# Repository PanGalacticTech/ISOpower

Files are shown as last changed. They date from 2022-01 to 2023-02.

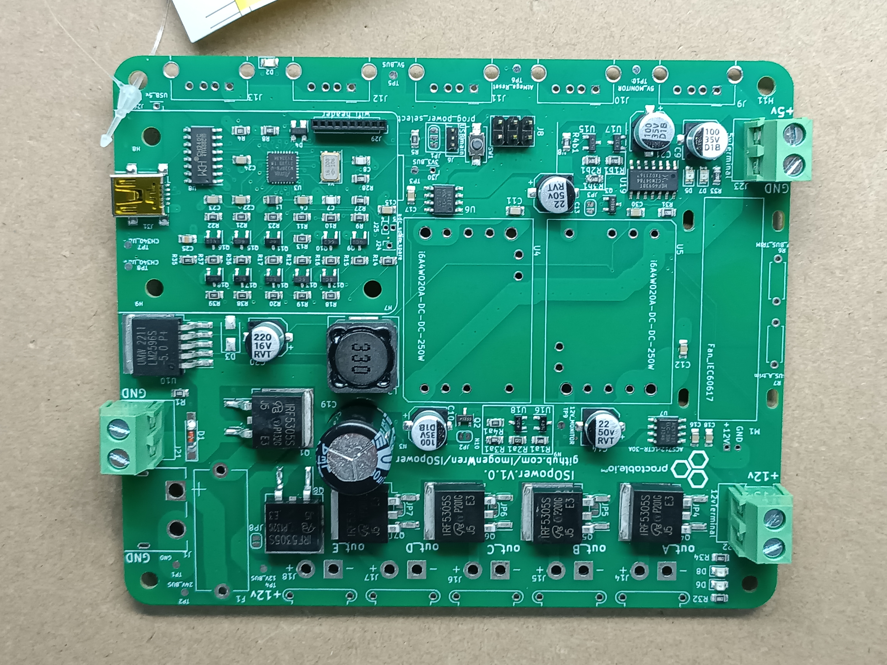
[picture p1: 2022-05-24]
Fabrication/Production Photos/Sample pictures of order T-Y4W418135A/IMG_20220523_194754.jpg

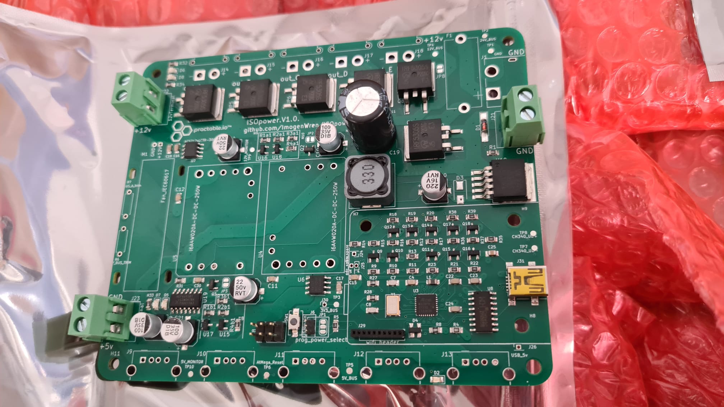
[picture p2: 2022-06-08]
Fabrication/Production Photos/Delivered Boards/ISOpower PCBs Delivered (1).jpeg

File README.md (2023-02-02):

# ISOpowerProject
 Remote power control board for ISO experiment containers, used for remote labs projects
ISOpower
ISOpowerPCBdesign

## Use

### Programming [See Issues]
 To Program AtMega328pb use the following settings:
 

### prog_power_select

- Jumper is used for power routing during programming
- Cut trace to main and solder USB to center to enable USB power during programming.
- Ensure to remove USB side and replace main for normal use

## Issues V1.0

1. Tx & Rx Pin swapped on CH340 - aTmeGA328P
 - To enable USB communication, reverse pins 2 & 3

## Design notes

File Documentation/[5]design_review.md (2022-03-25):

# PCB Design Review - [Project Title] 

_A form to document and record the PCB design review after completing layout in PCB editor._ 

## Design Review Notes

1. What Verification & Validation checks have been/can be carried out?
2. DRC Violations?
3. Will design solve problems?

## DRC - Design Rules Check

_Note down any DRC failings, the solution to remove them or reason for ignoring_

#### Errors

6 Courtyard overlap Errors
 - No solution required as conflicting footprint is surface level & unpopulated.

#### Warnings

1 Track has unconnected end
 - Copper layer is acting as heatsink
 
4 Footprint has no courtyard
 - Applies to silkscreen logos only - Can be ignored.

## Required Documentation for Fabrication

For PCB Fabrication:

	- Gerber files - In zipped folder [^gerber]

For PCB Fabrication, with component population:
	
	- Gerber files - in zipped folder [^gerber]
	- BOM [^1]
	- CPL Component Placement List / PNP Pick & Place File[^2]

### Documentation Checklist

|PCB				| Folder		|Files				| Checked 	| Checked Via 	|
|----				|----			|----				|----		|----			|
|	ISOpowerPCB		|zipped gerbers	|F_Cu.gbr			|	[]		|				|
|					|				|In1_Cu.gbr			|	[]		|				|
|					|				|In2_Cu.gbr			|	[]		|				|
|					| 				|B_Cu.gbr			|	[]		|				|
|					|				|F_Mask.gbr			|	[]		|				|
|					|		 		|B_Mask.gbr			|	[]		|				|
|					|				|F_Silkscreen.gbr	|	[]		|				|
|					|				|B_Silkscreen.gbr	|	[]		|				|
|					| 				|F_Paste.gbr		|	[]		|				|
|					|				|B_Paste.gbr		|	[]		|				|
|					| 				|Edge_Cuts.gbr		|	[]		|				|
|					|				|PTH.drl			|	[]		|				|
|					|		 		|NPTH.drl			|	[]		|				|
|					|ISO_power_PCB	| BOM.csv			|	[]		| 			|
|					|ISO_power_PCB	| top-pos.csv		|	[]		| 				| 
|----				|----			|----				|	----	|----			|
|ISOpowerWiFi_PCB	|zipped gerbers	|F_Cu.gbr			|	[X]		|				|
|					|				|In1_Cu.gbr			|	[X]		|				|
|					|				|In2_Cu.gbr			|	[X]		|				|
|					| 				|B_Cu.gbr			|	[X]		|				|
|					|				|F_Mask.gbr			|	[X]		|				|
|					|		 		|B_Mask.gbr			|	[X]		|				|
|					|				|F_Silkscreen.gbr	|	[X]		|				|
|					|				|B_Silkscreen.gbr	|	[X]		|				|
|					| 				|F_Paste.gbr		|	[X]		|				|
|					|				|B_Paste.gbr		|	[X]		|				|
|					| 				|Edge_Cuts.gbr		|	[X]		|				|
|					|				|PTH.drl			|	[X]		|				|
|					|		 		|NPTH.drl			|	[X]		|				|
|					|ISO_wifi_PCB	| BOM.csv			|	[X]		|	All Parts In Stock JLC PCB			|
|					|ISO_wifi_PCB	| top-pos.csv		|	[X]		|	checked against BOM			|

## Fabrication Notes

- Keep track of Component Stock, is it required for external fabrication, or purchased seperatly for manual assembly?

- JLC offer for free, specific location for their manufacturing number. Specify with "JLCJLCJLCJLC" on the silkscreen level.

## TODO

# Notes

[^gerber]: List of commonly used file names & formats, accepted by the majority of fabrication houses:
			- F.CU

[^1]: BOM Bill Of Materials
Reccomended formats: .csv, .xls, .xlsx
Example:
| Comment	| Designator	| Footprint | JLCPCB Part # (optional) 	|
|---		|---			|---		|---						|
|	100nF	|  C1			| 0805		|C49678 					|
|	22u		|  C2-5			| 6.3x5.4	|C72505						|
|	100uF	|  C6, C8, C10	| 6.3x7.7	|C65221						|

[^2]: Pick & Place or CPL File <br>
The Pick & Place File must contain the information below:

-	Designator - Component Reference Designator (e.g. C1, L2, R3)
- 	Mid X/Mid Y - The X/Y coordinate of the component centroid. Recommended units: Metric(mm). 
-	Layer - Top / Bottom, the board side where the component should be placed. 
-	Rotation - The rotation of the component given in degrees. Positive values are counter clockwise.
-	Recommended File Format: .csv, .xls and .xlsx.
Example:
| Designator 	| Mid X 	| Mid Y 	| Layer 	| Rotation 	|
|--				|---		|---		|---		|---		|
|	C1			| 95.0518mm	|22.6822mm	|	T		|	270		|
|	C2 			| 106.4056mm|33.2342mm	|	B		| 	90		|

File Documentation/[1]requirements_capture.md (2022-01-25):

# [1]   Requirements Capture Form - [Project Title]

_This form is intended to assist in capturing the requirements for new Open Source Embedded Systems Projects, <br>
its scope & implementation can be adapted to suit projects of varying complexity._

***************************************************************************************************************************************************************
## [1.1]Project Brief
_The project brief should contain an outline of the proposed project, with enough detail to derive a comprehensive list of requirements. The format, layout and
information provided can be tailored to project complexity_

### Example Project Brief - [ISOpower]

> PCB required to host DC-DC converters, to convert 24V DC power supply into operating voltages for ISO Experimental containers. 
> The containers house 4 experiments, each requires 12v for motor power, and 5v for raspberry pi via USB.
> Each USB 5v channel requires a power switch that can be actuated remotely.
> 
> Total current draw for 12v & 5v bus should be monitored via a microcontroller, with a interface allowing control
> over power switches on the board.
> Additional 5v & 12v power channel is required for future proofing, additional control infrastructure etc.
> 
> LED indication of correct voltage for 24v, 12v & 5v bus.
> Cooling should be provided for DC/DC Converters.
> Estimated power requirements set out in sub-system specification below.

#### Sub-Systems Specifications
##### Power Requirements
_Specific requirements for subsystems can be documented at this stage_    <br>
> a. steady power usage of 20W 1.7A at 12V (Maxxon AMax 32 236668 Graphite brushes, 20 Watt)[Estimated value, may change in future iterations] <br>
> b. peak power usage of 69W 5.7A at 12V (when motor stalled)  [Estimated value, may change in future iterations] <br>
> c. 5V power for the Raspberry pis, typically 2.5A per Raspberry Pi; four raspberry pi connections, 1 connection for power to microcontroller monitoring chip. <br>

##### Interface Requirements
> d. User interaction with system should be via JSON formatted commands with the ability to both poll specific data, and actuate switches.
> e. The system should report its status once per second. Minimum data for status update includes:
>    1. Current sensor readiings for 5v & 12v bus
>    2. Time since last reset in seconds. (Hint: Record number of times millis() rollsover) Integer should be able to record times >10 years (314496000 seconds)
> f. Any network communication should use TCP protocol, on port 443 to avoid firewall conflicts.
> g. Off nominal voltage detection should trigger a JSON message to be sent to the user. This reporting should be rate limited to avoid a single fault sending spam.
> h. System should track, and allow to be queried remotly:
>    1. How many times has the voltage tripped for out of spec performance
>    2. The last recorded time of a voltage fault
>    3. Include method for resetting count to 0 after fault has been rectified.

#### General Specifications/Requirements
_These specifications are going to be valid for most projects developed using this framework_
> 4. Circuit should be protected from reverse supply voltages. <br>
> 5. Circuit should be fuse protected <br>
> 6. 5v bus should be protected from over voltage conditions.

#### Optional Features
_Any features or functions that are optional should be stated here_  <br>
>  1. Report Status & current usage for sustainabilty and maintainance purposes.
>  2. Individual remote control of channel power.
>  3. Use only connection types that can be operated with one hand. i.e. avoid screw terminals.

#### Design Optimisation
_What parameters of the design should be minimised/maximised?_

#### Design Tradeoffs
_Space for discussion and weighing up of features that may or may not be required_ <br>

> If method is implemented to turn off power in the case of fault condition, provide some way of bypassing this feature
> to assist in debugging.

#### Quality Assurance 
_What quality assurances or requirements, if any, need to be established?_

#### Notes
_Any Extra Notes?_
Software Reqirements: 

### Existing Products & COTS (Consumer Off The Shelf)
_The project brief may also contain information on currently available similar products and a brief description of the features they lack and a 
quick review of whether they can fullfill the aims of the project._

_______________________________________________________________________________________________________________________________________________________
## [1.2]High Level Requirements Description

*This section should contain a numbered list of all the specific high level requirements that can be gathered from the project brief, or from the client directly. <br>
High Level Requirements capture the intent and function of a system, without going into specifics of how these will be achieved or any specific implementations. I.E. They take a Black Box approach*

#### High Level Requirements should address:
> - Client Needs
> - Features & Functionality
> - Interfaces
> - Performance
> - Quality Attributes
> - Design Constraints
> - Regulations
> - Safety & Security
> - System

#### Requirements should be:
> - Specific           - Document a single feature or function requirement at a time.                                                 <br>
> - Quantifyable       - Provide quantifyable parameters, boundary limits of operation and/or design tolerences, rather than open ended specifications where possible.<br>
> - Self Contained     - Do not rely on assumptions to deliver information, as different engineers will make different assumptions, which may cause conflicts 
> - Traceable          - Assign each requirement an ID number, this will be used to trace any design decisions through the development process. <br>

_Good requirements are the foundation for successful development of a project, as it allows design decisions to be traced through the development process.
it also provides the information required to undertake successful **Verification** & **Validation**[^V&V]._ 

_______________________________________________________________________________________________________________________________________________________
## [1.3]Example Requirements Capture - [ISOpower]

> HL.1. DC/DC converters must be able to provide continuous current draw of 6.7A at 12V ~(80W) for motor power, from supplied 24v input.                   <br>
> HL.2. DC/DC converters must be able to provide peak current draw of 12A at 12V ~(144W) for motor power, from supplied 24v input, in case of stall condition.[^2]    <br>
> HL.3. USB power must be able to provide total of 12.5A @ 5v ~(62.5W), from supplied 24v input.                                  <br>
> HL.4. Each USB channel will have the ability to remotely disable and re-enable power.                                      <br>
> HL.5. Voltage & Current monitoring of 12v bus, accessable remotely.   <br>   <!-- This is a weak requirement, how often should data be sampled is a nessissary component of this requirement -->
> HL.6. Current monitoring of 5v bus, accessable remotely  <br>    <!-- This is a weak requirement, how often should data be sampled is a nessissary component of this requirement -->
> HL.7. Board must have push-fit or bayonet connectors for motors & offboard hardware. <br>
> HL.8. Power Board will have 5 * 12v outputs from 12v Bus. <br>
> HL.9. Power Board will have 5 * 5v outputs from 5v Bus. <br>
> HL.10. Power board will be protected from reversed supply voltages <br>
> HL.11. Power Board will be protected from over-current conditions<br>
> HL.12. PCB must have same footprint & mounting screwholes as V1, to aid in assembly <br>
> HL.13. 5v bus will be protected from over-voltage condition. <br>
> HL.14. Each power bus will display visual (LED) indication of correct operation or fault conditions (over/under voltage) <br>

<!-- NOTE: 
High level
Include a microcontroller which communicates over USB, with a JSON-based interface allowing control over any power switches on board, and can report any measurements made.
It is my understanding this is not a high level requirement, as it is a specific low level hardware & software requirement. I have modified some of the other requirements
 to make it clear that the data & power channel actuation should be accessable remotly, but have not gone into specifics of how that would be achieved-->

When to review? <br>
*High level requirements should undertake a review process,* ***Validation***, *to ensure they meet the clients needs, before any further development takes place.*<br> 

<!--After review, please see the next document in the design process* [[2]Low Level Requirements Capture](https://github.com/PanGalacticTech/project_template/blob/main/%5B2%5DLL_requirements_capture.md) -->

_______________________________________________________________________________________________________________________________________________________

[^V&V]: Verification & Validation - What is it? <br>
        - Verification - _"Does the implementation meet the requirements?"_ <br>
        - Validation   - _"Are the requirements correct"_
        
[^2]: Assumption made that only 1 motor will be in stall condition, with others running typically.

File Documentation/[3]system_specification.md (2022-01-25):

# [3]  System Specification - [Project Title]

_This form is intended to derive low level hardware & software specification from the ***Validated***  
High Level Requirements Capture Form [[1]requirements_capture.md](https://github.com/PanGalacticTech/project_template/blob/main/%5B1%5Drequirements_capture.md) and
[[2]system_optioneering.md](https://github.com/PanGalacticTech/project_template/blob/main/%5B2%5Dsystem_optioneering.md) <br>
Its scope can be adapted to suit projects of varying complexity_ <br>

****************************************************************************************************************************
## [2.2] System Specification Description

_System Specifications for Hardware & Software are derived from and traceable back to the High level Requirements. At this stage optioneering should be
complete, and the design direction finalised._

<!-- NOTE: Origionally I had this document specified as "Low Level Requirements" given past training I had on embedded systems development in aviation, however I 
think this approach was far in excess of what is required for this kind of project, so I have merged "low level requirements" and "system specification" into a single step -->

## [2.3]Example System Specification - [ISOpower]

### [2.3.1]Hardware Specification
_Hardware specification should outline specific hardware devices, circuit design and hardware archetectures chosen to meet high level requirements._

<!-- NOTE: Spreadsheet would be better for comparason of features of components but I see value in documenting major components here too? -->

_Hardware Specification may contain the following subsections:_
- Hardware Architecture
- Major Components - Can be specific or requirements set out for comparason of specific components
- Circuit Design
- Other

### Hardware Architecture & Description

**[HL.1, HL.2, HL.3]**
> The hardware will comprise of a single PCB to home the 2 DC/DC converter modules. 
> These require local fan cooling for which +12v power and mounting holes will be provided.

**[HL.7]**
> 24v Power input will be via XT60 Connector mounted directly on PCB. 

**[HL.5]**
> MCU will be AtMega328p integrated to PCB with ESP32-WROOM-32UE as a WiFi tranciever. MCU will take ADC readings from 2 [Allegro ACS712](https://www.sparkfun.com/datasheets/BreakoutBoards/0712.pdf) current sensing modules,
> one between the DC/DC module and the 12v bus, the other between the 2nd DC/DC module and the 5v bus. Each MCU 

**[HL.5, HL.6]** 
> A voltage divider will be used with an additional ADC input to monitor the voltage of the 12v bus. <br>
> - R1: 100k <br>
> - R2: 56k <br>
> This will allow measurements from 0v to ~14v to be measured by the microcontroller ADC, while limiting current draw to a few microamps.
> Input to the MCU will be protected by a 5.1v Zener diode, incase of voltage spikes greater than can be mitigated by the voltage divider.

**[HL.9, HL.4, HL.13]**
> The 5v Bus will be distributed to 5 USB outputs via individual high side MOSFET switches for each channel,
> these will be connected source to 5v bus, drain to USB output, and gate to the logic circuit used to 
> trigger a power shutoff condition.
> 
> Solder bridges will be provided on the PCB to bypass these MOSFETs, in the case they are not required.

**[HL.4, HL.13]**
> Logic circuit to control power to each 5v USB output will follow the following logic, if: <br>
> A = microcontroller digital pin (1 per channel, logic level HIGH = channel deactivated) <br>
> B = Voltage Monitoring circuit (1 per +5v Bus, logic level HIGH = off nominal voltage detected)  <br>
> C = Output to MOSFET gate (1 per channel, logic level HIGH = MOSFET OFF state) <br>

> IF A OR B == HIGH: C = HIGH.

**[HL.13]**
> The voltage protection circuit will comprise of 2 TL431 Voltage reference ICs set as a window comparator. This circuit will
> output logic level LOW in the case +5V_BUS is pulled off nominal. (4.6v - 5.5v).
> 

**[HL.7, HL.8]**
> 12v bus power will be distributed to 5 XT30 connectors, mounted directly on the PCB. 

 **[HL.10]**
> Reverse voltage protection will be acheived via a P channel MOSFET[^RevVolt] at +Vcc in.

**[HL.11]**
> The system will be protected from overcurrent conditions by a 20A fuse between Vcc in+ and 24v bus. 

**[HL.12]**
> PCB dimensions will be 100x120mm. 

**[HL.14]**
> LM3916 Dot graph drive IC will be used on each voltage bus, 5v, 12v and 24v. Some experimentation may be required to select the correct
> circuit layout & resistor selection for each application. 24v bus will require additional voltage divider,<br>
> R1: 100k <br>
> R2: 56k <br>
> to scale voltage to correct input for LED driver. 24Vin =~ 8.6Vout

_Optional:_
> The PCB will contain footprints to allow 12v outputs to be switched via additional MOSFETs, as well as solder bridges to enable the PCB to be used without. [Dependent on overall size & space left after all other requirements have been met]

-----------------------------------------------------------------------------------------------------
### Major Components

#### DC/DC Converters
##### Option 1: <br>
**Non-Isolated DC-DC Converter, 3.3 → 15V dc Output, 20A**
| Attribute          	|  Value 	                            |  Notes
|---	                |---	                                |---
| **Part Number:**   	| I6A4W020A033V-001-R               	| 
| **Supplier:**     	| RS Components                      	|   
| **Vin:**          	| 9 - 40v                            	|   	
| **Vout:**           |  3.3 - 24v                          |   
|**Power:**            |    250W                            |     
| **Price:**           |  £44.66                            |   
| **URL:**              | https://uk.rs-online.com/web/p/non-isolated-dc-dc-converters/1813289    |     
| **Notes:**           | -     |    
|**Requirements Met:**  |  (HL.1, HL.2, HL.3)        |

#### P-Channel MOSFET for Channel Switching
_Use: High side power switch_
1. Switching of 5v USB power from bus to individual outputs
2. Switching of 12v power from bus to individual outputs (optional feature)
3. MOSFET is ON when gate is @ 0v, OFF when gate is driven to VDD

_Component Requirements:_
| Attribute | Value        | Notes |
|---        |---           |---    |
| Vds        | > (-)21V      | Drain/Source Breakdown Voltage = Operating Voltage + 70% |
|Id         | > (-)6A        | Max Continuous Drain Current > Stall Current of Motor |
| Vgs       | ~ -4.5       | Gate - Source Threshold Voltage[^Vgs] |
| Rds(on)   | <2 ohm       | Static Drain-to-Source-ON-Resistance[^Rds] @ Vgs |

_In the case the requirements for a component are known, however the specific part is unknown, it would be best to use a [spreadsheet](https://github.com/PanGalacticTech/project_template/blob/main/%5B2A%5Dcomponent_compare.xlsx) to weigh up alternative options._

##### Option 1: <br>
**IRF5305PBF P Channel MOSFET**
|Attribute        | Value                                            |Suitable  | Notes |
|---              |---                                               |---       |---    |
|Part Number:     |  IRF5305PBF                                      |          |       |
|Supplier:        | Farnell                                          | [x]      |       |                 
|Vds              |  -55V                                            | [x]      |       |     
|Id               |  -31A                                            | [x]      |       |  
|Rds(on) @ -10v   |  0.06                                            | [x]      |       |      
|Price:           |  £2.088                                          | [x]      |       |      
|                 |                                                  |          |       |
|URL:             |  [IRF5305PBF - Farnell](https://uk.farnell.com/infineon/irf5305pbf/mosfet-p-55v-31a-to-220/dp/8648255) |         |        |
|Availability     |   In Stock                                       | [x]       |       |
|Notes:           |  |         |       |                                                                            
|Meets Requirements: |                                               | [x]     |       |

#### P-Channel MOSFET for Reverse Volatage Protection
_Use: Reverse voltage protection_
1. MOSFET is ON when gate is @ 0v, OFF when gate is driven to VDD

_Component Requirements:_
| Attribute | Value        | Notes |
|---        |---           |---    |
| Vds        | > (-)21V      | Drain/Source Breakdown Voltage = Operating Voltage + 70% |
|Id         | > (-)6A        | Max Continuous Drain Current > Stall Current of Motor |
| Vgs       | ~ -4.5       | Gate - Source Threshold Voltage[^Vgs] |
| Rds(on)   | <2 ohm       | Static Drain-to-Source-ON-Resistance[^Rds] @ Vgs |

_In the case the requirements for a component are known, however the specific part is unknown, it would be best to use a [spreadsheet](https://github.com/PanGalacticTech/project_template/blob/main/%5B2A%5Dcomponent_compare.xlsx) to weigh up alternative options._

##### Option 1: <br>
**IRF5305PBF P Channel MOSFET**
|Attribute        | Value                                            |Suitable  | Notes |
|---              |---                                               |---       |---    |
|Part Number:     |  IRF5305PBF                                      |          |       |
|Supplier:        | Farnell                                          | [x]      |       |                 
|Vds              |  -55V                                            | [x]      |       |     
|Id               |  -31A                                            | [x]      |       |  
|Rds(on) @ -10v   |  0.06                                            | [x]      |       |      
|Price:           |  £2.088                                          | [x]      |       |      
|                 |                                                  |          |       |
|URL:             |  [IRF5305PBF - Farnell](https://uk.farnell.com/infineon/irf5305pbf/mosfet-p-55v-31a-to-220/dp/8648255) |         |        |
|Availability     |   In Stock                                       | [x]       |       |
|Notes:           |   DO NOT USE FOR REVERSE POWER PROTECTION ON 24V BUS. Vgs Max is 20v|         |       |                                                                            
|Meets Requirements: |                                               | [x]     |       |

#### AtMega328P MCU

#### Allego ACS712

#### 
-----------------------------------------------------------------------------------------------------

### Circuit Design & Schematic
_Final Circuit Design, Schematics & Justifications for design_

_____________________________________________________________________________________________________
 
#### [2.3.2]Software Specification

_Specify the software requirements, functions, frameworks and tools required to meet the high level requirements_

#### Tools:
| Tool | Purpose | Justification |
|---   |---      |---            |
|Arduino IDE| Software Development | Speed & ease of development for Arduino IoT functions |
|C++ | Programming Language | Native to Arduino environment |
|InfluxDB | Remote storage of power consumption data | Ease of setup & ease of posting data from remote devices |
|Grafana  | Graphic display of power consumption via web interface | off the shelf solution that can integrate control methods for sending HTTP requests back to controller |

### Software Specification

- ADC Samples of current sensor will be taken every 250mS  <!-- Let me know if these timings are suitable  -->
- ADC samples of 12v bus voltage will be taken every 250mS <!-- Let me know if these timings are suitable  -->
- Power Channel MOSFETS are "Active Low" Therefore channels will be turned off driven by a HIGH pulse from microcontroller.
- Seperate API for each power channel "on", "off" and "restart",

When to review? 
*System Specification should undertake a review process, to ensure the design meets the clients needs before moving to ***Fabrication*** <br>*

_______________________________________________________________________________________________________________________________________________________

### [2.4] Requirement Matrix

_Info On Requirements Matrix & Link to: [Requirements Matrix Document](https://broken_link.com)_

_______________________________________________________________________________________________________________________________________________________
#### References

- [Rugged Circuits: 10 Ways to Destroy an Arduino](https://www.rugged-circuits.com/10-ways-to-destroy-an-arduino)
- [High Side vs Low Side Switch](https://www.baldengineer.com/low-side-vs-high-side-transistor-switch.html)
- [Important Stuff: MOSFET Specs You Need to Know](https://www.embeddedrelated.com/showarticle/809.php)
- [Using the Atmel ATmega328P Analog to Digital Conversion Module](https://ece-classes.usc.edu/ee459/library/documents/ADC.pdf)

*******************************************************************************************************************************************************

#### Notes
**VGS & Rds Explanation**

_Assuming That_

|Attribute | Value | Max Current Flow
|---|---|---|
| Source Voltage | 5v |
|Rds(on) @ Vgs -4.5v | 0.0133 ohm      | 5/0.0133 = 376A |
|Rds(on) @ Vgs -10v   | 0.0083 ohm      | 5/0.0093 = 537A  |

#### Footnotes

[^Rds]: Drain-to-Source On-Resistance <br>
        - If current required is 2.5A, then R=5/2.5: R=2ohm absolute max Rds during operation (in practice must be much lower)   <br>
        - If Vcc = 5v, and gate is pulled to 0v GND, then Vgs ~-5v                                                                <br>
        - Datasheet shows Rds(on) @ Vgs -4.5 will be ~ 0.0133 ohm                                                                     <br>
        - If Vcc = 12v & Gate is pulled to 0v GND, then Vgs ~ -10v therefore Rds(on) ~ 0.0093 ohm                                                       <br>
        - HOWEVER, controller can only provide 5v so will need drivers to fully turn off MOSFET, see[^Vgs(th)]                              <br>

[^Vgs(th)]: Gate-Source Threshold Voltage <br>
            - Datasheet shows that Vgs must be >-2.0V to turn off device  <br>
            - i.e. Id = -250 uA @ Vds (Maximum Drain - Source voltage differential) <br>
            - Therefore if VCC is 12v, Gate Voltage must be driven to >10v to turn off MOSFET <br>

[^V&V]: Verification & Validation - What is it? <br>
        - Verification - _"Does the implementation meet the requirements?"_ <br>
        - Validation   - _"Are the requirements correct"_
        
<!--[^2]: Ruggeduino >5v cutoff circuit -->
      <!-- - ![image](https://user-images.githubusercontent.com/53580358/148758688-282c6b19-230f-4211-98ce-a5ba380fc2d2.png) -->
          
<!-- [^3]: Estimated current consumption of cutoff circuit
      - R = 17kohm, V = 5v. 
      - I=V/R
      - I = (17k / 5) = [2.9\*10^-4] A -->
      
[1v1]: [Arduino: Analog Reference](https://www.arduino.cc/reference/en/language/functions/analog-io/analogreference/)

[^RevVolt]: [Infineon Reverse Voltage Protection Methods](https://www.infineon.com/dgdl/Reverse-Batery-Protection-Rev2.pdf?fileId=db3a304412b407950112b41887722615) <br>
             

[^zener]: [Designing overvoltage protection using zener diodes](https://components101.com/articles/designing-an-overvoltage-protection-circuit-using-zener-diodes)

[^comp]: [op-amp comparator](https://www.electronics-tutorials.ws/opamp/op-amp-comparator.html)

[^vu]: [Single Transistor LED VU meter](https://electronicsarea.com/6-led-vu-meter-using-one-transistor/) <br>

[^uvov]: [LM431 Datasheet](https://www.ti.com/lit/ds/symlink/lm431.pdf?HQS=dis-dk-null-digikeymode-dsf-pf-null-wwe&ts=1642092638827&ref_url=https%253A%252F%252Fwww.ti.com%252Fgeneral%252Fdocs%252Fsuppproductinfo.tsp%253FdistId%253D10%2526gotoUrl%253Dhttps%253A%252F%252Fwww.ti.com%252Flit%252Fgpn%252Flm431) <br>  <br>
<!-- ![image](https://user-images.githubusercontent.com/53580358/149550148-76459666-dd3e-4661-bf27-dfcf147a4180.png) <br> -->

[^tl431]: Voltage Window Calculations: <br>
          - Vh=(1+(R2/R)1)*Vref   <br>
          - Vl=(1+(R4/R3))*Vref

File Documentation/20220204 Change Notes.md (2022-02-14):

# Change Notes

04/02/2022
As per discussion 26/01/22
1. Changed per channel 5v MOSFET switches to MOSFET control of DC/DC module on/off pin - due to failure of MOSFET switching during testing.
2. Added 5v buck converter for independent MCU_5V power bus.
	- Ensured all 5v MCU hardware is powered from common MCU_5V bus.
3. Removed circuit from NC pins on DC/DC modules.
4. Changed ESP32 USB interface to CH340
5. Changed MCU serial logic level converters from MOSFET to IC - TXS0102DCT
	- TODO: OE pin now requires low signal untill DC/DC supply is stable - Does it? Can it just be tied to 5v bus with a large capacitor? Does it need MCU to hold pin low untill 5V_BUS is stable?
6. Removed redundent 3V3_IN to power distribution page.
	- Rechecked all sheets for redundent pins, it won't impact drawing traces, but it will impact readability.
7. Added Mechanical layer as hirarchical sheet.
8. Moved voltage monitoring circuits to hirarchical sheet
9. Added voltage monitoring with TL431DBZ to 12V_BUS
10. Automatic shutoff circuit removed, as this would prevent the DC/DC module from powering on. Instead moved to AtMega328p digital inputs
and microcontroller will control shutdown of DC/DC supply if out of spec voltage detected.
		- This is a severe limitation compared to the specification, and this also does not prevent damage to devices on 5V_BUS if voltage is pulled high, for example to 12v due to user error.
		- TODO: Add independent overvoltage protection to 5V_BUS? 		[Zener Diode Overvoltage Protection - Sparkfun](https://www.rs-online.com/designspark/how-does-zener-diode-do-overvoltage-protection-in-circuit#:~:text=In%20order%20to%20protect%20the,flow%20in%20the%20reverse%20direction).
11. Changed logic level conversion for 12v outputs to 12v drive circuit. [12v drive circuit](https://forum.arduino.cc/t/easiest-way-of-driving-amplifying-from-5v-to-12v/123290)
12. Added proto pin connections for ESP MCU.
13. Changed 20v Zener in reverse voltage protection to 18v

## TODO
- TODO: OE pin now requires low signal untill DC/DC supply is stable - Does it? Can it just be tied to 5v bus with a large capacitor? Does it need MCU to hold pin low untill 5V_BUS is stable?
- TODO: Add independent overvoltage protection to 5V_BUS? 		[Zener Diode Overvoltage Protection - Sparkfun](https://www.rs-online.com/designspark/how-does-zener-diode-do-overvoltage-protection-in-circuit#:~:text=In%20order%20to%20protect%20the,flow%20in%20the%20reverse%20direction).
PROBLEM: Suggested 100r resistor between 5v and raspberry pi, this limits current to 50mA, raspi requires min 400mA (Tested with raspi 512mb, raspi4 will likely require more current) if R=12.5 is selected, Imax would be 400mA, however power disspation in the resistor is now 0.4\*5 = 2W.
- TODO: Nominal Voltage Indication?

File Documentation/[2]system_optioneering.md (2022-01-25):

# [2]  System Optioneering - [Project Title]

_This form is intended to assist in optioneering to derive low level hardware & software specification from the ***Validated***  
High Level Requirements Capture Form [[1]requirements_capture.md](https://github.com/PanGalacticTech/project_template/blob/main/%5B1%5Drequirements_capture.md).
Its scope can be adapted to suit projects of varying complexity_ <br> 
*******************************************************************************************************************************************************

## [2.1] Design Tradeoffs & Optioneering
_Space to work through different options before deciding on specific low level requirements & system specification for hardware & software
It is useful to highlight situations where one design decision is dependent on other decisions, or where a design decision will have known, or forseeable impacts on
other decisions later._

### Preamble
_Introduction to the design approach if required_ <br>

### Optioneering Diagrams
_Flowcharts can be used to explore the relationships between different options, and display graphically how making specific design decisions
will affect the other available options._

hardware optioneering diagram
_Flowchart showing the different communications standards and methods that could be used to connect the user interface and the microcontroller, dependent on
low level hardware choices_

### Optioneering Table
_This is an example of the options that may wish to be explored for this project, however there may be alternative ways of displaying this information
that are more suitable_

|Requirement| Function                      | Options                       | Sub-Options                                | Hirarchy  | Notes  |
|---        | ---------------------------   | ---------------------------   | -----------------------------------------  | -------   |----    |
|HL:(4,5,6) | Controller for Current Sensing| Integrated MCU on PCB         | CH340 Driver for USB comms to Raspi        |    3      |        |
|"          |           "                   |           "                   | ublox Wifi module & remote database server |    2      |        |
|"          |           "                   |           "                   | ESP32 performs as MCU controller And/Or Wifi Module|    1   |  requires 3.3v logic if used as MCU|
|"          |           "                   | Arduino Nano 33 IoT| Local Raspberry Pi |    4    | will require 8 port switch to accomidate extra RasPi in ISO Container | 
|"          |           "                   |    "             | Remote Raspberry Pi  |    3    | Will Require external WiFi Antenna to ensure robust Connection|
|           |                               |                               |                                            |           |        |
|HL:(4)     | Power Switching               |N-Channel Low Side MOSFET      |                                            |    3      |        |  
|"          |           "                   |P-Channel High Side MOSFET     |                                            |    1      | Difficult to source suitable MOSFET|  
|"          |           "                   |Relay                          | Normally Closed                            |    2      | Expense       |    
|"          |           "                   |           "                   | Latching                                   |    4      | Expense, Reliability       |      
|           |                               |                               |                                            |           |        |  
|HL:(1,2,3) | Power Supply DC/DC Conversion | COTS Modules                  |                                            |     1     |        |    
|"          |           "                   | ReEngineer & Integrate w/ PCB |                                            |     4     |        |  
|"          |                               |                               |                                            |           |        |
|HL:(7)     | Power Input Connector         | Screw Terminals               |       |  4  |                                             |
|"          |         "                     | XT60 - 60A  Connector         |       |  1  | Quick Disconnect Compared to screw terminals, easy to solder, easier PCB mounting|
|           |                               |                               |                                            |           |        |  
|HL:(7)     | 12v Power Output Connectors   | 2.1mm Barrel Jacks            |       |  4  | Hard to find with range of options, easy to damage|
|"          |           "                   | XT30 - 30A Connector          |       |  1  | Easy to source, many differnt options, well defined specifications|
|           |                               |                               |                                            |           |        |  
|HL:(5)     | Voltage Sensing               | Voltage Divider on 12 bus   | | 1 | Can't be used for 5v bus as MCU would share Vcc ref. Must protect MCU from voltage spikes|
|"          |     "                         | Voltage sense IC            | | 2 | Cant find suitable option, open for reccomendations, could be used for both 12v and 5v bus|
------------------------------------------------------------------------------------------------------------------------------------------------------------------------------

### Circuit Design & Hardware Optioneering [Hardware]
_Exploration of circuit elements & Hardware that might be used to meet design objectives_

#### Overvoltage Protection of 5v USB Bus ***[HL.13]***
_The aim of overvoltage protection for the 5v bus, is to protect the raspberry pis in the event +12v power is accidently applied to this bus, pulling all the outputs to 12v
and causing damage. Several possible approaches will be discussed below_

##### Approach 1 - Zener Diode

>    5.1v zener diode reverse biased between the USB outputs 5v rail, and GND.
>    A 100ohm resistor must be between the potential source of over voltage and the zener diode.[^zener]

***Problems with this approach***

>    If the source of the overvoltage is also on the USB bus, this does not nessissarily solve the problem,
>    as the current will flow unimpeded through the zener diode, causing overheating and component failure. 
>    If it fails open circuit (likely) then the protection is no longer active and the 5v bus will be pulled to 12v.

> As the likely source of the overvoltage would be the other USB inputs, each V+ rail would need a 100ohm resistor, with a zener diode on the supply side of the resistor.

##### Approach 2 - Using the MOSFET That is Already There

>    As the USB channel is already designed to be switched off via a logic high signal (+5v) from a microcontroller, 
>    could that same MOSTFET also be triggered with logic high if a fault condition is detected?
>    This solution would have to be passive, i.e not be reliant on the MCU to trigger, as this
>    would delay response and would not stop damage from occuring.
>     <br>
>     A logical OR gate could be used to provide a buffer between the logic HIGH/LOW pin on the microcontroller, and the
>     other system for providing a logical HIGH in the case the 5v bus moves out of tolerance. 1 logical OR gate would be required for each USB output,
>     The output of each logic gate, feeds the gate of each MOSFET

***OverVoltage Detection***

> Voltage Supivisor/detection ICs: <br>
> [TL431 Voltage Reference, Adjustable Shunt](https://uk.farnell.com/on-semiconductor/tl431acdg/voltage-ref-shunt-2-495v-36v-soic/dp/1651199)<br>
>  Voltage is monitored on 5v rail, and IC outputs a logic high if voltage goes outside of set nominal band. <br>
>  
> **Use Case**
> [TI TL431 for Under & Overvoltage Detection]( https://www.ti.com/lit/an/slva987a/slva987a.pdf?ts=1642107195143&ref_url=https%253A%252F%252Fwww.google.com%252F)[^uvov]
> In this case, the V(high) and V(low) thresholds are set via 4 resistors. Calculations outlined below[^tl431] 

> TL431 has a minimum cathode current of 1mA, so resistor selection must be checked to meet this requirement.

> Resistor Values Estimated:
> R1: 470r      <br>
> R2: 560r     <br>
> Vhigh ~ 5.47v   <br>
> <br>
> R3: 560r   <br>
> R4: 470r   <br>
> Vlow ~ 4.8v
>
> R5 = 220r <br>
> <br>
> Using these values & <br> I = (Vcc - Vref)/R3 (High edge) & I = (Vcc - Vref)/R5 (Low edge) [No sure if correct best guess given forum posts & datasheet] <br>ere
> Ika ~ 4mA for high edge & 11mA for low edge

***Implementing This Solution***
> Requires: <br>
> 5 * OR Gates <br>
> > <br>
> To make these gates from common gates, it would require: <br>
> 15 * NAND Gates. (3 req for OR gate) <br>
> OR <br>
> 10 * NOR Gates. (2 req for OR gate) <br>
> Suggest: <br> 
> 3 * [MC74HC02ADG SMD Quad Input NOR Gate](https://uk.farnell.com/on-semiconductor/mc74hc02adg/ic-74hc-cmos-smd-74hc02-soic14/dp/9666893)

---

#### Power Bus Visual Fault Indications ***[HL.14]***
_The aim of this requirement is to provide additional information to engineers testing, maintaining and debugging the system. For this
reason it should be independent of all other systems, and simplified as much as possible._

>   I much prefer the idea of independent indication for each bus, rather than a traffic light with 
>   "All Nominal" "Something Off Nominal" "Everything Off Nominal" indication, as I believe this is; <br>
>   1: less useful than say "A Okay" "B Okay" "C Okay" indications and <br>
>   2: it may also be harder to design if we take a passive approach, i.e: This system should work independently
>   of any microcontrollers.

##### Option 1

>   A window comparator circuit[^comp] could be used to display whether each bus is falling within a predefined "nominal" window,
>   however this circuit would be reliant on stable Vcc, so is not useful for detecting if Vcc is off nominal.
>   An independent linear or LDO regulator could provide independent reference voltages to solve this problem, but 
>   increase in cost & complexity.

##### Option 2

> Led VU Meter, Options detailed [^vu]  [LM3916 Dot/Bar Display Driver](https://cdn.sparkfun.com/datasheets/Components/General%20IC/lm3916.pdf) Monitors 
> analog voltage level and lights up to 10 LEDs sequentially
> Supply Voltage from 3v to 25v - Suggest it runs from 12v rail for each use case. Input can handle from 0 to 35v 

***Assessment***
This option did not work well, as the window for the "okay" LED was far too wide, I managed to get it to indicate high voltage at 5.5v, however getting it to register
low voltage at anything >4v seemed to fail. It also did not perform well with off nominal supply voltage.

#### Option 3
> Use the features of the DC/DC supplies[^dcdc]

> DC/DC supply can indicate an off nominal voltage rail by pulling a logic HIGH to ground. This can be monitored by the MCU and set error LEDs. This will also enable easy 
> reporting & monitoring of power status.
> Can be used for visual indication lEDs & report via JSON.

---

#### MCU Selection

The best options for MCU seem to be either;
[AtMega328p](https://uk.farnell.com/microchip/atmega328p-an/mcu-8bit-atmega-20mhz-tqfp-32/dp/2443178?st=ATmega328P) combined with CH340 for USB comms & programming, ISP header for programming bootloaders, and an WiFi transcever as a peripheral device, or <br>

[ESP32-WROOM-32U](https://www.mouser.co.uk/ProductDetail/Espressif-Systems/ESP32-WROOM-32UM113DH3200UH3Q0?qs=W%2FMpXkg%252BdQ4Fqx%2FReRQpFQ==&mgh=1&vip=1&gclid=CjwKCAiAxJSPBhAoEiwAeO_fPwE6kImUAnBTI5SyodKJNS7nNKTfdQ13Md3OplGP5AphD8abym4PYBoCbGkQAvD_BwE), with the same USB interface and ISP header, but without the need for an additional WiFi transcever. This has a number of advantages and disadvantages. 

The major disadvantage is the ESP's requirement for 3.3v logic, this will likely require additional drivers for actuation of the MOSFET switches,
as well as voltage dividers and additional scaling on ADC inputs from the [ACS712 Hall Effect Linear Current Sensor](https://www.sparkfun.com/datasheets/BreakoutBoards/0712.pdf)
For this reason, using the AtMega328p as the main MCU seems like it will cause less issues with the rest of the circuit design.

However the selection of the peripheral WiFi adaptor throws up an ironic aside, it seems much cheaper to use ESP32
as a WiFi device than sourcing dedicated WiFi transceiver modules like the ublox nina.
The ESP32 is available with the option to connect an external antenna, which makes the system more adaptable for use
in areas that may not have adiquate WiFi signal with the antenna obscured inside a metal box.

***Conclusion***

The board will use both AtMega328p to act as the hardware controller, and ESP32 to act as wifi & higher level control. This will also act as a proving ground for using 
mixed controller boards, interfacing ESP32 with other MCUs, and potentually offering up the ability to expand the scope of the power supply module later with more advanced 
software run on the ESP32, with the AtMega handling the lower level hardware monitoring.

[Info on using ESP32 as WiFi adaptor for AtMega328p](https://icircuit.net/arduino-interfacing-arduino-uno-esp32/2134)[^esp32]

****************************************************************************************************************************

### Software Design & Optioneering [Software]
_Exploration of software, firmware and development tools that might be used to meet design objectives and test system performance_

### Software Structure Optioneering

#### Option A

- Arduino running state machine framework
- websocket server responds to HTTP GET requests for control of power channels
- concurrently taking analogRead() of 2 ADC inputs, and sending to external database with HTTP POST requests over wifi
- Data is pulled from database using graphing tool, like Grafana, which is built around a web accessable user interface.

#### Option B

- Arduino running state machine framework
- websocket server responds to HTTP GET requests 
- concurrently taking analogRead() of 2 ADC inputs, and sending to Raspberry Pi over USB communication.
- Raspberry pi requires script to place data received over COM port into web accessable format. 

#### Option C

- Arduino running state machine framework
- [Interfacing using JSON formatted data](https://github.com/dpreid/pidui/issues/5)
- concurrently taking analogRead() of 2 ADC inputs, and sending to client as JSON formatted data.
- Ties into existing infrastructre

_______________________________________________________________________________________________________________________________________________________

### [2.4] Requirement Matrix

_Info On Requirements Matrix & Link to: [Requirements Matrix Document](https://broken_link.com)_

_______________________________________________________________________________________________________________________________________________________
#### References

- [Rugged Circuits: 10 Ways to Destroy an Arduino](https://www.rugged-circuits.com/10-ways-to-destroy-an-arduino)
- [High Side vs Low Side Switch](https://www.baldengineer.com/low-side-vs-high-side-transistor-switch.html)
- [Important Stuff: MOSFET Specs You Need to Know](https://www.embeddedrelated.com/showarticle/809.php)
- [Using the Atmel ATmega328P Analog to Digital Conversion Module](https://ece-classes.usc.edu/ee459/library/documents/ADC.pdf)

*******************************************************************************************************************************************************

#### Notes

**VGS & Rds Explanation**

_Assuming That_

|Attribute | Value | Max Current Flow
|---|---|---|
| Source Voltage | 5v |
|Rds(on) @ Vgs -4.5v | 0.0133 ohm      | 5/0.0133 = 376A |
|Rds(on) @ Vgs -10v   | 0.0083 ohm      | 5/0.0093 = 537A  |

#### Footnotes

[^Rds]: Drain-to-Source On-Resistance <br>
        - If current required is 2.5A, then R=5/2.5: R=2ohm absolute max Rds during operation (in practice must be much lower)   <br>
        - If Vcc = 5v, and gate is pulled to 0v GND, then Vgs ~-5v                                                                <br>
        - Datasheet shows Rds(on) @ Vgs -4.5 will be ~ 0.0133 ohm                                                                     <br>
        - If Vcc = 12v & Gate is pulled to 0v GND, then Vgs ~ -10v therefore Rds(on) ~ 0.0093 ohm                                                       <br>
        - HOWEVER, controller can only provide 5v so will need drivers to fully turn off MOSFET, see[^Vgs(th)]                              <br>

[^Vgs(th)]: Gate-Source Threshold Voltage <br>
            - Datasheet shows that Vgs must be >-2.0V to turn off device  <br>
            - i.e. Id = -250 uA @ Vds (Maximum Drain - Source voltage differential) <br>
            - Therefore if VCC is 12v, Gate Voltage must be driven to >10v to turn off MOSFET <br>

[^V&V]: Verification & Validation - What is it? <br>
        - Verification - _"Does the implementation meet the requirements?"_ <br>
        - Validation   - _"Are the requirements correct"_
        
<!--[^2]: Ruggeduino >5v cutoff circuit -->
      <!-- - ![image](https://user-images.githubusercontent.com/53580358/148758688-282c6b19-230f-4211-98ce-a5ba380fc2d2.png) -->
          
<!-- [^3]: Estimated current consumption of cutoff circuit
      - R = 17kohm, V = 5v. 
      - I=V/R
      - I = (17k / 5) = [2.9\*10^-4] A -->
      
[^1v1]: [Arduino: Analog Reference](https://www.arduino.cc/reference/en/language/functions/analog-io/analogreference/)

[^RevVolt]: [Infineon Reverse Voltage Protection Methods](https://www.infineon.com/dgdl/Reverse-Batery-Protection-Rev2.pdf?fileId=db3a304412b407950112b41887722615) <br>
             

[^zener]: [Designing overvoltage protection using zener diodes](https://components101.com/articles/designing-an-overvoltage-protection-circuit-using-zener-diodes)

[^comp]: [op-amp comparator](https://www.electronics-tutorials.ws/opamp/op-amp-comparator.html)

[^vu]: [Single Transistor LED VU meter](https://electronicsarea.com/6-led-vu-meter-using-one-transistor/) <br>

[^uvov]: [LM431 Datasheet](https://www.ti.com/lit/ds/symlink/lm431.pdf?HQS=dis-dk-null-digikeymode-dsf-pf-null-wwe&ts=1642092638827&ref_url=https%253A%252F%252Fwww.ti.com%252Fgeneral%252Fdocs%252Fsuppproductinfo.tsp%253FdistId%253D10%2526gotoUrl%253Dhttps%253A%252F%252Fwww.ti.com%252Flit%252Fgpn%252Flm431) <br>  <br>
<!-- ![image](https://user-images.githubusercontent.com/53580358/149550148-76459666-dd3e-4661-bf27-dfcf147a4180.png) <br> -->

[^tl431]: Voltage Window Calculations: <br>
          - Vh=(1+(R2/R)1)*Vref   <br>
          - Vl=(1+(R4/R3))*Vref

[^dcdc]: [i6a4w_spec](https://product.tdk.com/en/system/files?file=dam/doc/product/power/switching-power/dc-dc-converter/specification/i6a4w_spec.pdf)

[^esp32]: <br>

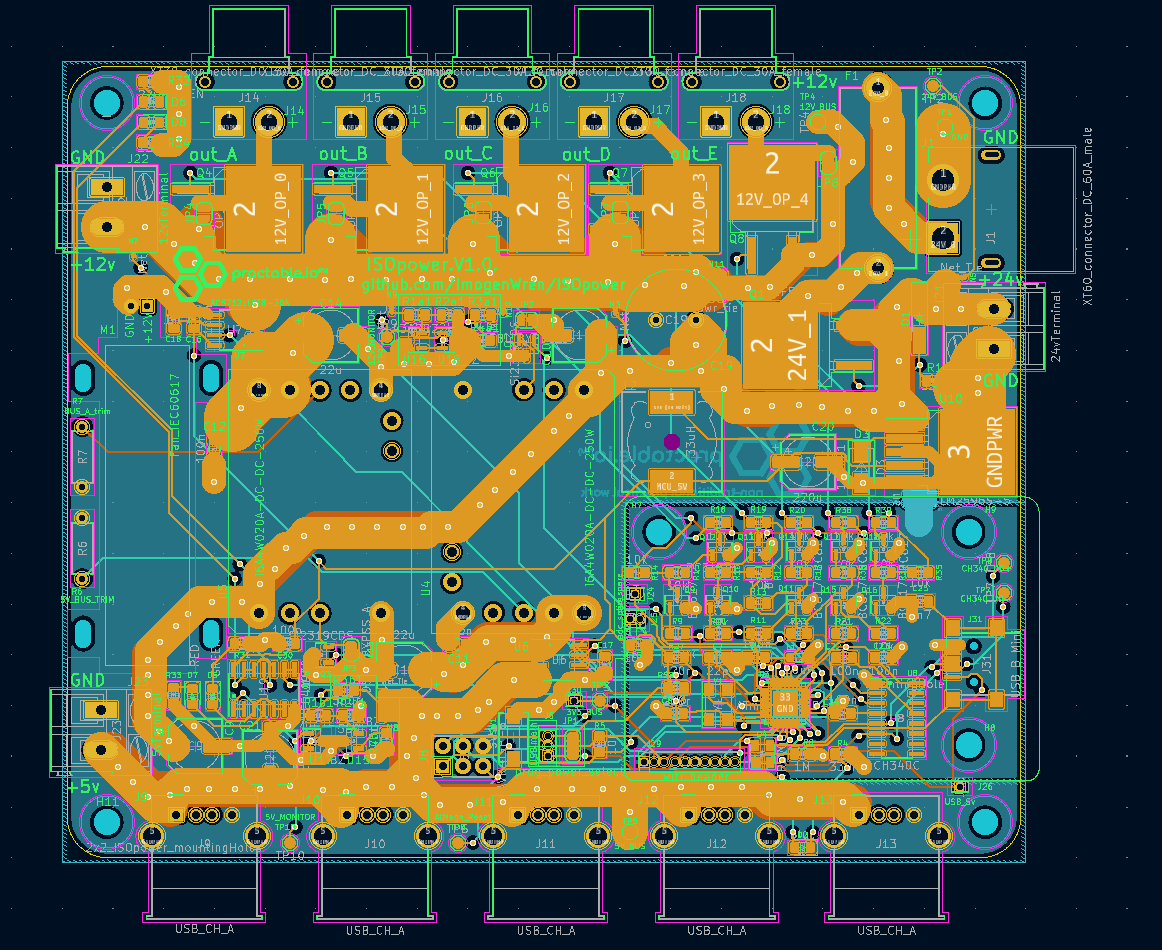
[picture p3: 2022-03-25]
Documentation/Media/ISOpowerPCBdesign.png

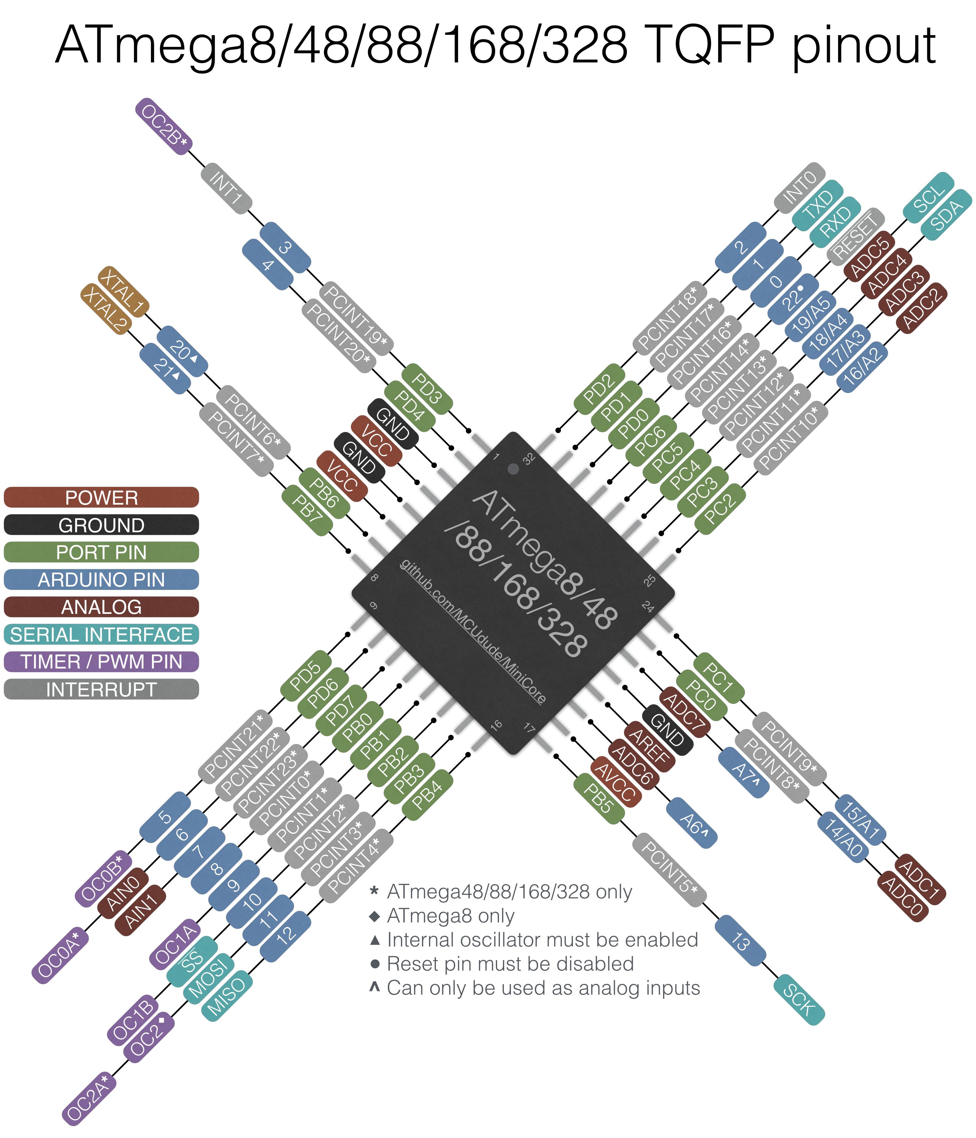
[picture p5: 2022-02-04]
Documentation/Media/MCU Pinouts/AtMega328.jpg

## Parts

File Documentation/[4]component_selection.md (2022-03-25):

# Component Selection & PCB Specification - [Project Title]

_A form to document and record specific part selections and PCB specifications for use during the PCB layout, and with PCB fabrication services like JLC PCB._ 

## Pre-PCB Layout Process

1. Verify schematic is correct.
2. Use Reference Designator tool to assign parts numbers to schematic symbols.
3. Perform Electrical Rules Check - NOTE: There will always be some errors & warnings that are unable to be cleared, this is not a problem as long as each one can be justified for your use case.
4. Assign footprints, use specified parts & JLCpcb parts library to cross check selected components against suitable item in parts libary. This will ensure that selected part is attainable and cost effective before moving onto layout.
5. Assign footprints to each component using the assign footprints tool. Use the [Component Selection] section of this form to assist in picking the correct parts & footprints. It is helpful
to gather specific parts numbers and suppliers at this stage.
6. Define net classes in Eschema using [File] > [Schematic Setup] > {Project} -> [Net Classes]. See [Net Classes]() below.
	- Note: This is only viewable on the schematic for now. Don't change line thickness, but different colours can be used to make sure net classes are being assigned correctly.
	- When we move into PCB layout we can define the thickness required for each net class.
7. Open PCB in board editor.

## Component Selections Notes

_This document should be filled in alongside assigning footprints in eschema, to ensure that the correct footprints have been selected before moving to PCB layout. At this stage of the 
design process, it is important to consider fabrication and start colating information that will be required by the fabrication house._

#### Tips & Considerations:

1. Check advantages of TH or SMD/SMT, especially regarding electrolytic capacitors, cost of component Vs Ease of Sourcing Vs Cost/Time to Manufacture should be considered.

2. Consider the advantages of automated assembly Vs Hand Soldered components. for JLC:
	- Hand soldering fee is: $3.5 + ($0.02 PER JOIN)
		- 1 extra day of assembly time.
		- "We accept the single-sided placement, so parts for manual and SMT assembly only can be placed on the same side."
	- SMT setup fee is: $8.00 + ($0.0015 PER JOIN)
	
	SMT is a higher initial cost, but lower per join. For current design, there are ~ 600 Joins, so cost is:
	- [Board Cost] + [Stencil?maybe] + [$8 SMT SETUP] + [600 * $0.0015] + [Component Costs] + [Shipping] = Board Cost + $8.90 + Components + shipping
	For TH heavy design using same number of components:
	- [Board Cost] + [$3.5 HAND SOLDERING] + [600 * $0.02] + [Component Costs] + [Shipping] = Board Cost + $15.5 + Components + shipping

3. Cost difference between Basic & Extended parts from JLC parts library
	- "When a part from the Extended Components Library is used, the operator needs to mount the feeders manually,
		which increases the labor cost, ***we charge $3 per extended component.***"
		
	- This represents the largest potential for cost saving by trying to use basic parts as often as possible over extended parts.
		
4. Minimum order quantity: If a part is used that has a MOQ of 100, and the board uses 1, you will be charged for 100. Double check and try and source components with a MOQ that is suitable for
the quantity of parts you actually require.

5. What is Ext price? - Only relivent if adding components to personal parts library @ JLC. In this case MOQ is usually by "the reel" and is often in multiples of 1000.

6. Consider the information and Files needed for SMT assembly.
	- Gerber files [^gerber]
	- BOM [^1]
	- CPL Component Placement List / PNP Pick & Place File[^2]

## Components

_Components & Parts selection table_

#### JLC Sourced Components

| Type					|Value	| Footprint | Price(pU)	|Min Quantity	| Price(min Q)	|JLC Part No|Vmax	| SMD/TH 	|Basic Part?|
|---					|---	|---		|---		|---			|---			|---		|--		|---		|			|
|Film/MLCC				| 100n	| 0805		|0.0046		|	4000		|				|C49678		|100	|	SMD		|	Yes		|
|Film/MLCC				| 22n	| 0805		|0.0112		|	4000 or 20	| 0.0112		|C1804		|50		|	SMD		|	Yes		|
|Electrolytic Capacitor | 100u 	| 6.3x7.7	|0.0895		| 	900			| 80.55			|C65221		|35		|	SMD		|			|
|Electrolytic Capacitor | 22u	| 6.3x5.4	|0.0383		|  	1000 or 10?	| 38.3			|C72505		|50		|	SMD 	|			|	
|Film/MLCC				| 1n	| 0805		|0.0076		| 	4000 or 20? | 30.4			|C46653		|50		|	SMD		|	Yes		|
|Electrolytic Capacitor	| 680u	| 12.5x20	|0.2914		|	100 or 1?	| 29.14			|C270015	|50		| 	TH		|			|
|Electrolytic Capacitor	| 220u	| 6.3x7.7	|0.0467		|	1000 or 10	| 46.7			|C2887273	|16		| 	SMD		|	Yes		|
|Film/MLCC				| 4n7	| 0805		|0.0054		| 	4000 or 20? | 21.6			|C1744		|50		|	SMD		|	Yes		|
|Zener Diode			| 18v 	| MINIMELF	|0.0289		|	2500 or 20	|	72?			|C410854	|19.1	|	SMD		|			|	
|LED					| Blue	| 0805		|0.038		|	3000		|	114?		|C138557	| n/a	|	SMD		|			|
|Schottky Diode 1N5821	|SS36-E3| DO-214AB	|0.3063 	|	850 or 2	|  255!?!		|C35722		| 60	| 	SMD		|	Yes	 	| Used D_SMA Footprint
|PRTR5V0U2X				|		| SOT-143	|0.0649		|	3000 or 10	| 				|C2827688	|		|	SMD		|			|
|LED					|Green	| 0805		|0.0178		|				|				|C84257		|		|	SMD		|			|	
|LED					|Red	| 0805		|0.0123		|				|				|C84256		|		|	SMD		|	Yes		| 
|USB Connector			| A   	| USB-A-TH	|0.0343		|	100 or 20	|	3.43		|C46406		|		|	TH		|			|
|USB Connector			|Mini B | USB mini-B - Lumburg|0.0615|	1000 or 10 | 61.5		|C2681563	|		|	SMD		|			|
|Inductor				|10uH	| 0805		|0.0166		|	4000 or 20	| 64			|C1046		|		|	SMD		|	Yes		|
|Inductor				|33uH	| 12x12x8	|0.3181		| 500 or 1		|159.05			|C339951	|		| 	SMD		|  			|
|Power MOSFET			|IRF5305|TO-263-2	|1.1936		|	50 or 1		| 55.			|C878890	|		|	SMD		|			|
|NPN BJT				|BC817	| SOT-23	|0.0177		|3000 or 50		| 53.0			|C181151	|		|	SMD		|			|	
|PNP BJT				|BC807	| SOT-23	|0.0271		|3000 or 50		| 53.0			|C8587		|		|	SMD		|	Yes		|
|Resistors				|10k	| 0805		| 			|				|				|C17414		|		|			|			|
|Resistors				|1k		| 0805		| 			|				|				|C17513		|		|			|			|
|Resistors				|330r	| 0805		| 			|				|				|C17630		|		|			|			|
|Tactile Switch Pushbutton|SPST	| EVQPE1	|0.0544		| 4000 or 10	|  217.6		|C455280	|		|	SMD		|			|
|ESP32-WROOM-32U		|		|ESP32-		|4.0605		|	650 or 1	|	2600		|C328062	|		|	SMD		|			|
|AMS1117-3.3 3V3 LDO	|3V3	| SOT-223-3_TabPin2	|0.1734	|2500		|				|C6186		|		|	SMD		|	Yes		|
|AtMega328p-MU			|		|QFN-32		|8.9386		|490 or 1		| expense		|C967933	|		|	SMD		| 			|
|ACS712xLCTR			|		|SOIC-8_3.9x4.9x1.27|2.8912|3000 or 1	| much expense	|C10681		|		|	SMD		|			|
|LM2596S-5				|5vFixed|TO-263-5	|0.7778		|500 or 1		|MuchExpenseWow	|C347421	|		|	SMD		| 			|
|CH340				|	|SOP/SOIC-16_3.9x10.1x1.27P|0.8454|50 or 1		|				|C84681		|		|	SMD		|			|
|TXS0102DTC			|	|SSOP-82.8x3.0x0.65	|0.5977		|3000 or 1		|				|C324082	|		|	SMD		|			|
|TL431					|		|SOT23-3	|0.0394		|3000 or 15		|				|C181103	|		|	SMD	 	|			|
|HEF4093 NAND Gate Shmitt|		|SOIC-14_3.9x8.7x1.27|0.2356|2500 or 1	|				|C7867		|		|	SMD		|			|
|5032-4P Xtal			|16MHz	|Xtal_SMD_abracon_ABM3C-4p_5.0x3.2|0.4071|1000 or 1|	|C242216	|		|	SMD		|			|
|MOSFET					|SI2301CDS|SOT-23-3	|0.0941		|	3000 or 15	|				|C10487		|		|	SMD		|	Yes		|

So far 23 extended components @ $3 each = $69 extra fee for component loading in pick & place machine.

#### Parts Options
_Alternative options for components that have been rejected_

| Type					|Value	| Footprint | Price(pU)	|Min Quantity	| Price(min Q)	|JLC Part No|Vmax	| SMD/TH 	|Basic Part?|Reason Against|
|---					|---	|---		|---		|---			|---			|---		|--		|---		|---		|---		|
|Tactile Switch pushbutton|SPST	|SW4_5.1x5.1x5.1|0.0169	|4000 or 5		|	67.6		|C318884	|		|	SMD		|	Yes		|	No suitable Footprint		|
|AtMega328p-AU			|		|TQFP-32_7x7mm_P0.8mm|8.9386|490 or 1	| expense		|C14877		|		|	SMD		| 	Yes		|	16 dollars! |

#### Externally Sourced Components
_Components that must be sourced seperatly due to stock @ JLC or due to cost difference_ 

_Note: Components purchased seperatly will need to be assembled by the client, JLC will not accept 3rd party components for their in house fabrication service._

| Type 			| Value | Footprint 	| Price(pu)	| Min Q	| Price (Min Q)	|	Supplier 		| Supplier ID 	| Link 	|
|---			|---	|---			|---		|---	|---			|---				|---			|---	|	
| XT60			| male	| custom		|			|		|				|					|				|		|
| XT30			| female| AMASS_XT30PW-F|1.34		|1		|1.34			|Switch Electronics	|482193			|https://www.switchelectronics.co.uk/female-xt60pw-gold-plated-connector-30a-amass |
| Fuse/Holder	|		|				|			|		|				|					|				|		|
| Fan			| 40\*10.5mm|Fan12v12V_40by10.5mm|	|		|				|					|				|		|
| Screw Terminal?|||||||||

## Net Classes
_List Net Classes & Specifications._

1oz Copper = ~35 um (0.035mm)
2oz Copper = ~70 um   

All trace width calculations assume:
- Trace Thickness to be 0.070mm
- External Conductors

 **THIS DESIGN REQUIRES 2oz Copper for external layers!**
 
 In order to lower the operating temperature, high current BUS will be routed over 2 layers and stiched with vias, however calculations
 are performed assuming JUST the external conductor layer.
 
 Formula used:
 
 I = K * dT^(0.44) * (W * H)^(0.725)
 
 Where:
 
 I = Max Current (A)
 dT = Temperature rise above ambient (degC)
 W = width (mil)
 H = Thickness/height (mil)
 K = Constant for Internal Traces (0.024) or External Traces (0.048)

_all distances in mm_

| Bus/Net Class		| Type 	| Vmax	| Vtyp 	| Imax 	| Ityp 	| Pmax	| Ptyp	|dt	|Width	|Clearance	|Vias	|Colour	| Notes |
|----				|----	|----	|----	|----	|----	|----	|----	|---|----	|----		|----	|----	|----	|
| Default			|Signal	| 	12	|	5	|		|		|		|		|20	|0.2	| 	0.2		| 0.8	|Default|		|		
| GND				|Power	|	0	|	0	|	16	| 6.16	|		|		|20	|2.5	|	0.2		| 	" 	|Brown 	|	|
| PWR_GND			|Power	| 	0	|	0	| 28.83	|		|	346	|150.9	|20	| 6.5	|	0.2		|		|RedBrown		|Same power requirements as 24V_BUS			|
|DIGITAL_GND		|Power	|	5	| 	0	|	n/a	|		|		|		|20	|0.3	|			|		|Grey		|		|
| MID_PWR_BUS		|Power	|		|		|   12	|		|		|		|20	| 3		|			|		|bright Yellow| For power bus connections near end of long runs - ensure no more than 2 per|
| 24V_BUS			|Power	|	30	|	24	| 14.4	| 6.16	|	346	| 147.9	|20	|4		|	0.2		|	"	|Red	|24v must be able to provide sum total of all other power bus		|
| 12V_BUS			|Power	|	12	|	12	| 20.83	| 10.2	|	250	| 122.4	|20	|6.5	|	0.2		|	"	|Orange	|Imax is @ max power available from DC/DC - Unlikely condition	|
| 5V_BUS			|Power	|	5	|	5	| 16	| 4.8	|	81	| 24	|20	|4.5	|	0.2		|	"	|Yellow	|Imax assumes 6x raspi drawing 2.5A, typical is 0.4-0.8A	|
| MCU_5V_BUS		|Power	|	5	|	5	| 3		| 0.5	|	15	| 1.5	|20	|0.3	|	0.2		|	"	|Lime	|max taken from max available from large wall plug USB chargers	|
| USB_PBUS			|Power	|	"	|	"	| "		|  "	|	"	| " 	|20	|0.3	|	0.2		|	"	|Aqua	|Same as above Not included in 24v calcs	|
| Digital			|Data	|	5	|	2.5	|	n/a	|	n/a	|	n/a	|	n/a	|20	|0.2	|	0.2		|	"	|Purple	|		|
| CURRENT_SENSOR	|Power	|	12	|	12	|20.83	|	10.2|		|		|20	|7		|	0.2		|	"	|Blue	| High Current + Low Temp Rise Required + Heatsink		|
| ANALOG			|Analog |	5	|	2.5	| mA   	|  mA	|	n/a	|	n/a	|20	|0.2		|	0.2		|	"	|Pink	|		|
|PWR_OUTPUT			|Power	| 		|		| 8		|		|		|		|20	| 2		|			|		|		|	for one single high current OP	|

Trace Thicknesses have been modified during routing to account for DRM violations where tracks meet footprint pins. 
In each case judgement can be made, EG the 12v bus is specified for full 20A
current for 5x experimental outputs, however in order to fit everything on the PCB, this width must be ristricted where possible.

In this case, the last connections on this bus provide current to a single experimental output, so the trace has been specified for 12A, and 3mm width. 
This is still over specification for the requirements at this point on the bus, giving reassurance that it can perform within the required tolerances, leaving some spare capacity 
for future use cases.  

## PCB Layout Process

1. Group components by functional block and move them off to the side. 
2. Draw PCB outline.
2. Turn off GND nets using [Appearance] > [Nets] toolbar, as all grounds can connect directly to GND plane on bottom copper layer.
3. Place all mechanical hardware, I.E Any component that has a specific location to meet operational needs, line up with other PCBs, or enclosures, buttons that may need to be spaced
	specifically for ergonomic reasons etc.
4. Arrange functional blocks of components, minimising nets crossing and aiming to get joined pins as close to each other as possible.
5. Move functional blocks into free space on the PCB, taking care to minimise distances and number of nets that cross each other. This is not a perfect process, and no layout meets idealised
design parameters. Choose your priorites.
6. Rearrange components as needed to make the layout more efficient.
7. Once all components are placed on PCB, start running traces. Prioritise:
	- 1. High Power traces as they take up more space on the PCB
	- 2. Single components with a large number of connections (MCUs, large connectors, etc)
	- 3. Traces which cross large areas of the PCB.
	Deprioritise:
	- Short local connections, these will be easy to join later using free layers
	- Ground connections, any missing at the end can usually be easily joined using a short trace and via to GND plane.
	
	Note:
	- Avoid using B.Cu layeras much as possible, as we want a single GND plane to cover the entire back of the PCB with little breaks through it.
	- Use vias where needed, but bear in mind overuse can make tracing the circut difficult and messy.
	- Dont be afraid to delete all traces and start again - it usually takes me at least 3 starts before I can complete the circuit, and often this still requires large deletions and changes.

Repeat steps 6 & 7 until all nets except GNDs are joined with copper traces.

8. Use Add Filled Zone tool to fill B.Cu with a GND plane.
9. Use vias and short traces to join any remaining GND pads to GND plane.

10. Run DRC - Design Rules Check. Expect warnings and errors.

Repeat steps 6 - 10 until DRC is passed, or errors/warnings can be justified, eg. Soldermask & Silkscreen layers can intersect, however it will throw warnings.

11. Aestheic checks. Using the 3D viewer, ensure that silkscreen layer is legiable and has the information required. Add Text, graphics, anything else required for the correct fabrication.

## TODO

PCB Layout

# Notes

[^gerber]: List of commonly used file names & formats, accepted by the majority of fabrication houses:
			- F.CU

[^1]: BOM Bill Of Materials
Reccomended formats: .csv, .xls, .xlsx
Example:
| Comment	| Designator	| Footprint | JLCPCB Part # (optional) 	|
|---		|---			|---		|---						|
|	100nF	|  C1			| 0805		|C49678 					|
|	22u		|  C2-5			| 6.3x5.4	|C72505						|
|	100uF	|  C6, C8, C10	| 6.3x7.7	|C65221						|

[^2]: Pick & Place or CPL File <br>
The Pick & Place File must contain the information below:

-	Designator - Component Reference Designator (e.g. C1, L2, R3)
- 	Mid X/Mid Y - The X/Y coordinate of the component centroid. Recommended units: Metric(mm). 
-	Layer - Top / Bottom, the board side where the component should be placed. 
-	Rotation - The rotation of the component given in degrees. Positive values are counter clockwise.
-	Recommended File Format: .csv, .xls and .xlsx.
Example:
| Designator 	| Mid X 	| Mid Y 	| Layer 	| Rotation 	|
|--				|---		|---		|---		|---		|
|	C1			| 95.0518mm	|22.6822mm	|	T		|	270		|
|	C2 			| 106.4056mm|33.2342mm	|	B		| 	90		|

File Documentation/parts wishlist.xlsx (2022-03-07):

Type | Value | Footprint | | Price(pU) | Min Quantity | Price(min Q) | JLC Part No | Vmax | SMD/TH | Manufacturer | MFG Part # | Basic Part? | Additional Cost | Notes
Film/MLCC | 100n | 0805 | 0.0046 | 20 | 0.092 | C49678 | 100 | SMD |  |  | Yes | 0
Film/MLCC | 22n | 0805 | 0.0112 | 20 | 0.224 | C1804 |  | SMD |  |  | Yes | 0
Electrolytic Capacitor | 100u | 6.3x7.7 | 0.0895 | 900 | 80.55 | C65221 |  | SMD |  |  |  | 3
Electrolytic Capacitor | 22u | 6.3x5.4 | 0.0383 | 10 | 0.383 | C72505 |  | SMD |  |  |  | 3
Film/MLCC | 1n | 0805 | 0.0076 | 20 | 0.152 | C46653 |  | SMD |  |  | Yes | 0
Electrolytic Capacitor | 680u | 12.5x20 | 0.2914 | 1 | 0.2914 | C270015 |  | PTH |  |  |  | 3
Electrolytic Capacitor | 220u | 6.3x7.7 | 0.0467 | 10 | 0.467 | C2887273 |  | SMD |  |  | Yes | 0
Film/MLCC | 4n7 | 0805 | 0.0054 | 20 | 0.108 | C1744 |  | SMD |  |  | Yes | 0
Zener Diode | 18v | MINIMELF | 0.0289 | 20 | 0.578 | C410854 |  | SMD |  |  |  | 3
LED | Blue | 0805 | 0.0380 | 20 | 0.76 | C138557 |  | SMD |  |  |  | 3
Schottky Diode 1N5821 | SS36-E3 | DO-214AB | 0.3063 | 2 | 0.6126 | C35722 | 60 | SMD |  |  | Yes | 0
PRTR5V0U2X |  | SOT-143 | 0.0649 | 10 | 0.649 | C2827688 |  | SMD |  |  |  | 3
LED | green | 0805 | 0.0178 | 20 | 0.356 | C84257 |  | SMD |  |  |  | 3
LED | red | 0805 | 0.0123 | 20 | 0.246 | C84256 |  | SMD |  |  | Yes | 0
USB Connector | A | USB-A-TH | 0.0343 | 20 | 0.686 | C46406 |  | TH |  |  |  | 3
USB Connector | Mini B | USB mini-B - Lumburg | 0.0615 | 10 | 0.615 | C2681563 |  | SMD | SHOU HAN | MINI 5PTP |  | 3
Inductor | 10uH | 0805 | 0.0166 | 20 | 0.332 | C1046 |  | SMD | Sunlord | SDFL2012S100KTF | Yes | 0
Inductor | 33uH | 12x12x8 | 0.3181 | 20 | 6.362 | C339951 |  | SMD | YJYCOIN | YPRH1207-330M |  | 3
Power MOSFET | IRF5305 | TO-263-2 | 1.1936 | 20 | 23.872 | C878890 | 55 | SMD | VBsemi Elec | IRF5305STR
MOSFET P-Channel | SI2319CDS-T1-GE3 | SOT23-3 | 0.1069 | 15 | 1.6035 | C558254 |  | SMD | VBsemi Elec | SI2319CDS-T1-GE3 |  | 3
NPN BJT | BC817 | SOT-23 | 0.0177 | 20 | 0.354 | C181151 | 50 | SMD | Guangdong Hottech | BC817-40 | Yes | 0
PNP BJT | BC807 | SOT-23 | 0.0271 | 20 | 0.542 | C8587 | 50 | SMD |  |  |  | 3
Resistors | 10k | 0805 | 0.0222 | 20 | 0.444 | C17414 |  | SMD | UNI-ROYAL(Uniroyal Elec) | 0805W8F1002T5E |  | 3
Resistors | 1k | 0805 | 0.0222 | 20 | 0.444 | C17513 |  | SMD |  |  |  | 3
Resistors | 330r | 0805 | 0.0222 | 20 | 0.444 | C17630 |  | SMD | UNI-ROYAL(Uniroyal Elec) | 0805W8F3300T5E | Yes | 0
Resistors | 560r | 0805 | 0.0032 | 20 | 0.064 | C28636 |  | SMD | UNI-ROYAL(Uniroyal Elec) | 0805W8F5600T5E | Yes | 0
Resistors | 470r | 0805 | 0.0028 | 20 | 0.056 | C114564 |  | SMD | YAGEO | RC0805FR-07470RL | no | 3
Resistors | 2k0 | 0805 | 0.0027 | 20 | 0.054 | C17604 |  | SMD | UNI-ROYAL(Uniroyal Elec) | 0805W8F2001T5E | yes | 0
Resistors | 2k2 | 0805 | 0.0026 | 20 | 0.052 | C17520 |  | SMD | UNI-ROYAL(Uniroyal Elec) | 0805W8F2201T5E | Yes | 0
Resistors | 1M | 0805 | 0.0025 | 20 | 0.05 | C17514 |  | SMD | UNI-ROYAL(Uniroyal Elec) | 0805W8F1004T5E | Yes | 0
Resistors | 220r | 0805 | 0.0025 | 20 | 0.05 | C17557 |  | SMD | UNI-ROYAL(Uniroyal Elec) | 0805W8F2200T5E | Yes | 0
Tactile Switch Pushbutton | SPST | EVQPE1 | 0.0544 | 10 | 0.544 | C455280 |  | SMD | XUNPU | TS-1088R-02026 |  | 3
ESP32-WROOM-32U |  | ESP32- | 4.0605 | 1 | 4.0605 | C328062 |  | SMD |  |  |  | 3
AMS1117-3.3 3V3 LDO | 3V3 | SOT-223-3_TabPin2 | 0.1734 | 2500 | 433.5 | C6186 |  | SMD |  |  | Yes | 0
AtMega328p-MU |  | QFN-32 | 8.9386 | 1 | 8.9386 | C967933 |  | SMD | Microchip Tech | ATMEGA328PB-MU |  | 3
ACS712xLCTR |  | SOIC-8_3.9x4.9x1.27 | 2.8912 | 1 | 2.8912 | C9932 |  | SMD | Allegro MicroSystems, LLC | ACS712ELCTR-30A-T |  | 3
LM2596S-5 | 5Vfixed | TO-263-5 | 0.7778 | 1 | 0.7778 | C347421 |  | SMD | UMW(Youtai Semiconductor Co., Ltd.) | LM2596S-5.0 |  | 3
CH340 |  | SOP/SOIC-16_3.9x10.1x1.27P | 0.8454 | 1 | 0.8454 | C84681 |  | SMD | WCH(Jiangsu Qin Heng) | CH340C |  | 3
TXS0102DTC |  | SSOP-82.8x3.0x0.65 | 0.5977 | 1 | 0.5977 | C324082 |  | SMD |  |  |  | 3
TL431 |  | SOT23-3 | 0.0394 | 15 | 0.591 | C181103 |  | SMD |  |  |  | 3
HEF4093 NAND Gate Shmitt trigger |  | SOIC-14_3.9x8.7x1.27 | 0.2356 | 1 | 0.2356 | C7867 |  | SMD | Nexperia | HEF4093BT,653 |  | 3
5032-4P Xtal | 16MHz | Xtal_SMD_abracon_ABM3C-4p_5.0x3.2 | 0.4071 | 1 | 0.4071 | C242216 |  | SMD |  |  |  | 3
MOSFET | SI2301CDS | SOT-23-3 | 0.0941 | 15 | 1.4115 | C10487 |  | SMD |  |  | Yes | 0
1.27mm Pin Headers - Male | 3 pin | HDR-TH_3P-P1.27-V | 0.0255 | 1 | 0.0255 | C24980 |  | PTH | BOOMELE(Boom Precision Elec) | C24980 |  | 3
AVR-6pin-ISR header | 2x3pin | HDR-TH_6P-P2.54-V-R2-C3-S2.54_A2541WV-2X3P | 0.1282 | 1 | 0.1282 | C225518 |  | PTH | CJT(Changjiang Connectors) | A2541WV-2x3P
Screw Terminal | 2 pin | CONN-TH_2P-P5.08_DB128L-5.08-2P | 0.15350 | 1 | 0.1535 | C395868 |  | PTH | DIBO | DB128L-5.08-2P-GN-S |  |  | 18A
1.27mm Pin Headers - Female | 10 pin | HDR-TH_10P-P1.27-V-M | 0.1714 | 1 | 0.1714 | C124392 |  | PTH | Ckmtw(Shenzhen Cankemeng) | B-2201S10P-A121
 |  |  |  | Total | 576.7725 |  |  |  |  |  | Additional Costs | 78

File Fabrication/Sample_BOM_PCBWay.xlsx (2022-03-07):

 |  |  | xxxx xxxx xxxxx xxPCS BOM (Sample Bill of Materials)
Item # | *Designator | *Qty | Manufacturer | *Mfg Part # | Description / Value | *Package/Footprint | Type | Your Instructions / Notes
1 | U1 | 1 | Linear | LTC3780EG#PBF | IC BUCK-BOOST CONV 24-SSOP | 24-SSOP | SMD
2 | U2,U4 | 2 | Fairchild | LM2904M | IC OPAMP DUAL -40-85 C 8-SOIC | 8-SOIC | DNS
3 | U3 | 1 | ON | LM317MBDTG | LM317M IC REG VOLT ADJ 500MA DPAK | DPAK | SMD
4 | U5 | 1 | Microchip | PIC16F690-I/SS | IC PIC MCU FLASH 4KX14 20SSOP | 20SSOP | SMD
5 | Q1 | 1 | Diodes Inc | GBJ10005-F | RECT BRIDGE GPP 50V 10A GBJ | GBJ | SMD
6 | R14,R18 | 2 | Panasonic | ERJ-6ENF4701V | RES 4.70K OHM 1/8W 1% 0805 SMD | 0805 | SMD
7 | R15 | 1 | Susumu | RL3720WT-R022-F | RES .022 OHM 1W 1% 0815 SMD | 0815 | SMD
8 | R16, R31 | 2 | Panasonic | ERJ-6ENF4702V | RES 47.0K OHM 1/8W 1% 0805 SMD | 0805 | SMD
9 | C5 | 1 | Murata | GRM21BR71C225KA12L | CAP CER 2.2UF 16V X7R 0805 | 0805 | SMD
10 | C7 | 1 | Murata | GRM21BR71C475KA73L | CAP CER 4.7UF 16V X7R 0805 | 0805 | DNS
11 | C8,C22 | 2 | Muruta | GRM21BR71C105KA01L | CAP CER 1.0UF 16V 10% X7R 0805 | 0805 | SMD
12 | CN6 | 1 | Molex | 538-53398-0671 | 1.25mm Connectors VERTICAL HDR SMT 6P | SMT 6P | SMD
13 | L1,L2 | 2 | Coiltronics | DR127-150-R | INDUCTOR SHIELD PWR 15UH SMD | SMD | SMD
14 | L3 | 1 | TDK | ACM1211-102-2PL-TL | CHOKE COMM MODE 1000 OHM 6A SM | SMD | SMD
15 | CN3,CN4 | 2 | Molex | 53047-0510 | CONN HEADER 5POS 1.25MM VERT TIN | 5POS | thru-hole
Need a quick and accurante quote? Need an efficient production? Please read SMT Ordering Necessary Files & Info in 1 minute. Thank you very much! (https://www.pcbway.com/smt_ordering_guide.html)
Click for Instructions on How to Create a BOM (https://www.pcbway.com/blog/PCB_Assembly/How_to_Build_a_BOM__Bill_Of_Materials_.html)

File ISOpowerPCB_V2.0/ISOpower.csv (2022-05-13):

Source: | C:\Users\dheard\Documents\KiCad\Projects\ISOpower\ISOpowerPCB\ISOpower.kicad_sch
Date: | 25/03/2022 09:52
Tool: | Eeschema (6.0.0)
Generator: | C:\Program Files\KiCad\6.0\bin\scripting\plugins/bom_csv_grouped_by_value_with_fp.py
Component Count: | 149
Ref | Qnty | Value | Cmp name | Footprint | Description | Vendor
C4, C11, C12, C15, C16, C22, C23, C24, C30, | 9 | 100n | cap_film_0805 | Capacitor_SMD:C_0805_2012Metric_Pad1.18x1.45mm_HandSolder | Unpolarized capacitor
C7, C8, | 2 | 22p | cap_film_0805 | Capacitor_SMD:C_0805_2012Metric_Pad1.18x1.45mm_HandSolder | Unpolarized capacitor
C9, C10, C21, | 3 | 100u | 100u | Capacitor_SMD:CP_Elec_6.3x7.7 | Polarized capacitor
C13, C14, | 2 | 22u | 22u | Capacitor_SMD:CP_Elec_6.3x5.4 | Polarized capacitor
C17, C18, | 2 | 1n | cap_film_0805 | Capacitor_SMD:C_0805_2012Metric_Pad1.18x1.45mm_HandSolder | Unpolarized capacitor
C19, | 1 | 680u | 100u | Capacitor_THT:C_Radial_D12.5mm_H20.0mm_P5.00mm | Polarized capacitor
C20, | 1 | 220u | 100u | Capacitor_SMD:CP_Elec_6.3x7.7 | Polarized capacitor
C25, | 1 | 4n7 | cap_film_0805 | Capacitor_SMD:C_0805_2012Metric_Pad1.18x1.45mm_HandSolder | Unpolarized capacitor
D1, | 1 | BZV55B18 | BZV55B18 | Diode_SMD:D_MiniMELF_Handsoldering | 18V, 500mW, 2%, Zener diode, MiniMELF
D2, | 1 | Blue | LED_0805_smd | LED_SMD:LED_0805_2012Metric_Pad1.15x1.40mm_HandSolder | Light emitting diode
D3, | 1 | 1N5821 | 1N5821 | Diode_SMD:D_SMA | 30V 3A Schottky Barrier Rectifier Diode, DO-201AD
D4, | 1 | PRTR5V0U2X | PRTR5V0U2X | Package_TO_SOT_SMD:SOT-143 | Ultra low capacitance double rail-to-rail ESD protection diode, SOT-143
D5, D6, | 2 | GREEN | LED | LED_SMD:LED_0805_2012Metric_Pad1.15x1.40mm_HandSolder | Light emitting diode
D7, D8, | 2 | RED | LED | LED_SMD:LED_0805_2012Metric_Pad1.15x1.40mm_HandSolder | Light emitting diode
F1, | 1 | 20A | Fuse | Fuse:Fuseholder_Cylinder-5x20mm_Stelvio-Kontek_PTF78_Horizontal_Open | Fuse
H7, H8, H9, | 3 | MountingHole | MountingHole | MountingHole:MountingHole_3.2mm_M3 | Mounting Hole without connection
H11, | 1 | 2x2_ISOpower_mountingHoles | 2x2_ISOpower_mountingHoles | MountingHole:ISOpower_4xmounting_M3 | Mounting Hole without connection
J1, | 1 | XT60_connector_DC_60A_male | XT60_connector_DC_60A_male | Connector_AMASS:AMASS_XT60PW-M | Generic connector, single row, 01x02, script generated (kicad-library-utils/schlib/autogen/connector/)
J6, | 1 | prog_power_select | Conn_01x03_Male | Connector_PinHeader_1.27mm:PinHeader_1x03_P1.27mm_Vertical | Generic connector, single row, 01x03, script generated (kicad-library-utils/schlib/autogen/connector/)
J8, | 1 | AVR-ISP-6 | AVR-ISP-6 | Connector_PinHeader_1.27mm:PinHeader_2x03_P1.27mm_Vertical | Atmel 6-pin ISP connector
J9, J10, J11, J12, J13, | 5 | USB_CH_A | USB_A | Connector_USB:USB_A_Molex_67643_Horizontal | USB Type A connector
J14, J15, J16, J17, J18, | 5 | XT30_connector_DC_30A_female | XT30_connector_DC_30A_female | Connector_AMASS:AMASS_XT30PW-F_1x02_P2.50mm_Horizontal | Generic connector, single row, 01x02, script generated (kicad-library-utils/schlib/autogen/connector/)
J21, | 1 | 24vTerminal | Screw_Terminal_01x02 | TerminalBlock:TerminalBlock_Altech_AK300-2_P5.00mm | Generic screw terminal, single row, 01x02, script generated (kicad-library-utils/schlib/autogen/connector/)
J22, | 1 | 12vTerminal | Screw_Terminal_01x02 | TerminalBlock:TerminalBlock_Altech_AK300-2_P5.00mm | Generic screw terminal, single row, 01x02, script generated (kicad-library-utils/schlib/autogen/connector/)
J23, | 1 | 5vTerminal | Screw_Terminal_01x02 | TerminalBlock:TerminalBlock_Altech_AK300-2_P5.00mm | Generic screw terminal, single row, 01x02, script generated (kicad-library-utils/schlib/autogen/connector/)
J24, | 1 | dio_spare | Conn_01x01_Male | Connector_PinHeader_1.27mm:PinHeader_1x01_P1.27mm_Vertical | Generic connector, single row, 01x01, script generated (kicad-library-utils/schlib/autogen/connector/)
J25, | 1 | adc_spare | Conn_01x02_Male | Connector_PinHeader_1.27mm:PinHeader_1x02_P1.27mm_Vertical | Generic connector, single row, 01x02, script generated (kicad-library-utils/schlib/autogen/connector/)
J26, | 1 | USB_5v | Conn_01x01_Male | Connector_PinHeader_1.27mm:PinHeader_1x01_P1.27mm_Vertical | Generic connector, single row, 01x01, script generated (kicad-library-utils/schlib/autogen/connector/)
J29, | 1 | wifi_header | Conn_01x10_Female | Connector_PinSocket_1.27mm:PinSocket_1x10_P1.27mm_Vertical | Generic connector, single row, 01x10, script generated (kicad-library-utils/schlib/autogen/connector/)
J30, | 1 | 3V3_spare | Conn_01x01_Male | Connector_PinHeader_1.27mm:PinHeader_1x01_P1.27mm_Vertical | Generic connector, single row, 01x01, script generated (kicad-library-utils/schlib/autogen/connector/)
J31, | 1 | USB_B_Mini | USB_B_Mini | Connector_USB:USB_Mini-B_Lumberg_2486_01_Horizontal | USB Mini Type B connector
JP1, | 1 | prog_power_select | Jumper_3_Bridged12 | Jumper:SolderJumper-3_P1.3mm_Bridged12_RoundedPad1.0x1.5mm_NumberLabels | Jumper, 3-pole, pins 1+2 closed/bridged
JP2, | 1 | DSBL_BYPSS_B | SolderJumper_2_Open | Jumper:SolderJumper-2_P1.3mm_Open_RoundedPad1.0x1.5mm | Solder Jumper, 2-pole, open
JP3, | 1 | DSBL_BYPSS_A | SolderJumper_2_Open | Jumper:SolderJumper-2_P1.3mm_Open_RoundedPad1.0x1.5mm | Solder Jumper, 2-pole, open
JP4, | 1 | OP_0 | SolderJumper_2_Open | Jumper:SolderJumper-2_P1.3mm_Open_RoundedPad1.0x1.5mm | Solder Jumper, 2-pole, open
JP5, | 1 | OP_1 | SolderJumper_2_Open | Jumper:SolderJumper-2_P1.3mm_Open_RoundedPad1.0x1.5mm | Solder Jumper, 2-pole, open
JP6, | 1 | OP_2 | SolderJumper_2_Open | Jumper:SolderJumper-2_P1.3mm_Open_RoundedPad1.0x1.5mm | Solder Jumper, 2-pole, open
JP7, | 1 | OP_3 | SolderJumper_2_Open | Jumper:SolderJumper-2_P1.3mm_Open_RoundedPad1.0x1.5mm | Solder Jumper, 2-pole, open
JP8, | 1 | OP_4 | SolderJumper_2_Open | Jumper:SolderJumper-2_P1.3mm_Open_RoundedPad1.0x1.5mm | Solder Jumper, 2-pole, open
L1, | 1 | 10uH | L | Inductor_SMD:L_0805_2012Metric_Pad1.05x1.20mm_HandSolder | Inductor
L2, | 1 | 33uH | L | Inductor_SMD:L_12x12mm_H8mm | Inductor
M1, | 1 | Fan_IEC60617 | Fan_IEC60617 | ISOpower:Fan12V_40by10.5mm | Fan (according to IEC-60617)
Q1, Q4, Q5, Q6, Q7, Q8, | 6 | IRF5305_PBF | IRF5305_PBF | Package_TO_SOT_SMD:TO-263-2 | -31A Id, -55V Vds, Single P-Channel HEXFET Power MOSFET, 60mOhm Ron, TO-220AB
Q2, Q3, | 2 | Si2319CDS | Si2319CDS | Package_TO_SOT_SMD:SOT-23 | -4.4A Id, -40V Vds, P-Channel MOSFET, SOT-23
Q9, Q10, Q11, Q12, Q13, Q14, Q15, Q16, Q17, Q18, | 10 | BC817 | BC817 | Package_TO_SOT_SMD:SOT-23 | 0.8A Ic, 45V Vce, NPN Transistor, SOT-23
R1, R4, | 2 | 330r | Resistor_0805 | Resistor_SMD:R_0805_2012Metric_Pad1.20x1.40mm_HandSolder | Resistor
R1a1, | 1 | 560r | Resistor_0805 | Resistor_SMD:R_0805_2012Metric_Pad1.20x1.40mm_HandSolder | Resistor
R1b1, | 1 | 470r | Resistor_0805 | Resistor_SMD:R_0805_2012Metric_Pad1.20x1.40mm_HandSolder | Resistor
R2a1, | 1 | 2k2 | Resistor_0805 | Resistor_SMD:R_0805_2012Metric_Pad1.20x1.40mm_HandSolder | Resistor
R2b1, | 1 | 560r | Resistor_0805 | Resistor_SMD:R_0805_2012Metric_Pad1.20x1.40mm_HandSolder | Resistor
R3a1, | 1 | 560r | Resistor_0805 | Resistor_SMD:R_0805_2012Metric_Pad1.20x1.40mm_HandSolder | Resistor
R3b1, | 1 | 560r | Resistor_0805 | Resistor_SMD:R_0805_2012Metric_Pad1.20x1.40mm_HandSolder | Resistor
R4a1, | 1 | 2k0 | Resistor_0805 | Resistor_SMD:R_0805_2012Metric_Pad1.20x1.40mm_HandSolder | Resistor
R4b1, | 1 | 470r | Resistor_0805 | Resistor_SMD:R_0805_2012Metric_Pad1.20x1.40mm_HandSolder | Resistor
R5, R9, R10, R11, R12, R13, R14, R15, R16, R17, R18, R19, R20, R21, R22, R23, R35, R36, R37, R38, R39, | 21 | 10k | Resistor_0805 | Resistor_SMD:R_0805_2012Metric_Pad1.20x1.40mm_HandSolder | Resistor
R6, | 1 | 5V_BUS_TRIM | Resistor_0805 | Resistor_THT:R_Axial_DIN0207_L6.3mm_D2.5mm_P7.62mm_Horizontal | Resistor
R7, | 1 | BUS_A_trim | Resistor_0805 | Resistor_THT:R_Axial_DIN0207_L6.3mm_D2.5mm_P7.62mm_Horizontal | Resistor
R8, | 1 | 1M | Resistor_0805 | Resistor_SMD:R_0805_2012Metric_Pad1.20x1.40mm_HandSolder | Resistor
R27, R28, R31, R32, R33, R34, | 6 | 220r | Resistor_0805 | Resistor_SMD:R_0805_2012Metric_Pad1.20x1.40mm_HandSolder | Resistor
SW1, | 1 | SW_Push | SW_Push | Button_Switch_SMD:SW_SPST_EVQPE1 | Push button switch, generic, two pins
TP1, | 1 | GND | TestPoint | TestPoint:TestPoint_Pad_D1.5mm | test point
TP2, | 1 | 24V_BUS | TestPoint | TestPoint:TestPoint_Pad_D1.5mm | test point
TP3, | 1 | 3V3_BUS | TestPoint | TestPoint:TestPoint_Pad_D1.5mm | test point
TP4, | 1 | 12V_BUS | TestPoint | TestPoint:TestPoint_Pad_D1.5mm | test point
TP5, | 1 | 5V_BUS | TestPoint | TestPoint:TestPoint_Pad_D1.5mm | test point
TP6, | 1 | AtMega_Reset | TestPoint | TestPoint:TestPoint_Pad_D1.5mm | test point
TP7, | 1 | CH340_UD- | TestPoint | TestPoint:TestPoint_Pad_D1.5mm | test point
TP8, | 1 | CH340_UD+ | TestPoint | TestPoint:TestPoint_Pad_D1.5mm | test point
TP9, | 1 | 12V_MONITOR | TestPoint | TestPoint:TestPoint_Pad_D1.5mm | test point
TP10, | 1 | 5V_MONITOR | TestPoint | TestPoint:TestPoint_Pad_D1.5mm | test point
U3, | 1 | ATmega328PB-M | ATmega328PB-M | Package_DFN_QFN:QFN-32-1EP_5x5mm_P0.5mm_EP3.1x3.1mm | 20MHz, 32kB Flash, 2kB SRAM, 1kB EEPROM, QFN-32
U4, U5, | 2 | i6A4W020A-DC-DC-250W | i6A4W020A-DC-DC-250W | ISOpower:i6A4W-DIP | 250W 9-40v Input Non-Isolated DC-DC Converter
U6, U7, | 2 | ACS712xLCTR-30A | ACS712xLCTR-30A | Package_SO:SOIC-8_3.9x4.9mm_P1.27mm | Â±30A Bidirectional Hall-Effect Current Sensor, +5.0V supply, 66mV/A, SOIC-8
U8, | 1 | CH340C | CH340C | Package_SO:SOIC-16_3.9x9.9mm_P1.27mm | USB serial converter, UART, SOIC-16
U10, | 1 | LM2596S-5 | LM2596S-5 | Package_TO_SOT_SMD:TO-263-5_TabPin3 | 5V 3A Step-Down Voltage Regulator, TO-263
U15, U16, U17, U18, | 4 | TL431DBZ | TL431DBZ | Package_TO_SOT_SMD:SOT-23 | Shunt Regulator, SOT-23
U19, | 1 | HEF4093B | HEF4093B | Package_SO:SOIC-14_3.9x8.7mm_P1.27mm | Quad 2-Input NAND Schmitt Trigger, SOIC-14
Y1, | 1 | 16MHz | Crystal_GND24 | Crystal:Crystal_SMD_Abracon_ABM3C-4Pin_5.0x3.2mm | Four pin crystal, GND on pins 2 and 4

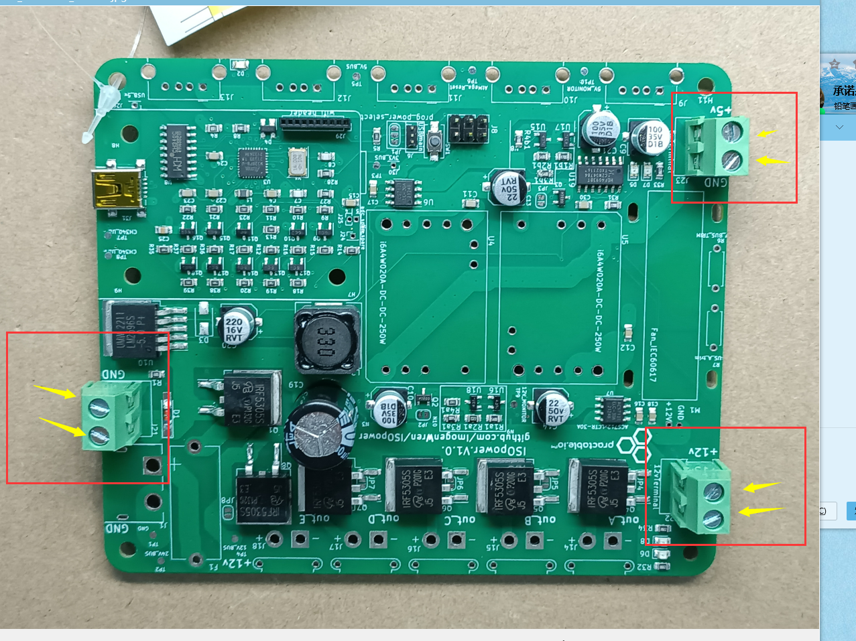
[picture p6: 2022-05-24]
Fabrication/Production Photos/Sample pictures of order T-Y4W418135A/The arrow indicates ternimal blocks port.png

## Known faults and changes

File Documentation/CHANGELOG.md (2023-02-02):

# ChangeLog

#### 04/02/2022
As per discussion 26/01/22
1. Changed per channel 5v MOSFET switches to MOSFET control of DC/DC module on/off pin - due to failure of MOSFET switching during testing.
2. Added 5v buck converter for independent MCU_5V power bus.
	- Ensured all 5v MCU hardware is powered from common MCU_5V bus.
3. Removed circuit from NC pins on DC/DC modules.
4. Changed ESP32 USB interface to CH340
5. Changed MCU serial logic level converters from MOSFET to IC - TXS0102DCT
	- TODO: OE pin now requires low signal untill DC/DC supply is stable - Does it? Can it just be tied to 5v bus with a large capacitor? Does it need MCU to hold pin low untill 5V_BUS is stable?
6. Removed redundent 3V3_IN to power distribution page.
	- Rechecked all sheets for redundent pins, it won't impact drawing traces, but it will impact readability.
7. Added Mechanical layer as hirarchical sheet.
8. Moved voltage monitoring circuits to hirarchical sheet
9. Added voltage monitoring with TL431DBZ to 12V_BUS
10. Automatic shutoff circuit removed, as this would prevent the DC/DC module from powering on. Instead moved to AtMega328p digital inputs
and microcontroller will control shutdown of DC/DC supply if out of spec voltage detected.
		- This is a severe limitation compared to the specification, and this also does not prevent damage to devices on 5V_BUS if voltage is pulled high, for example to 12v due to user error.
		-  Add independent overvoltage protection to 5V_BUS? < No reasons for decision below [^1]
		[Zener Diode Overvoltage Protection - Sparkfun](https://www.rs-online.com/designspark/how-does-zener-diode-do-overvoltage-protection-in-circuit#:~:text=In%20order%20to%20protect%20the,flow%20in%20the%20reverse%20direction).
11. Changed logic level conversion for 12v outputs to 12v drive circuit. [12v drive circuit](https://forum.arduino.cc/t/easiest-way-of-driving-amplifying-from-5v-to-12v/123290)
12. Added proto pin connections for ESP MCU.
13. Changed 20v Zener in reverse voltage protection to 18v

#### 16/02/2022
14. Added Nominal Voltage indication for 5v & 12v Bus
15. Added capacitor to OE pin on logic level converter and tied pin to 3v3

#### 22/02/22
16. Changed logic level conversion circuit based on pspice analysis of previous circuit.

#### 23/02/2022

17. Reevaluated board with both microcontrollers on daughterboard. This is unfortunatly still not going to fit, however, by moving the AtMega & Associated hardware back onto the main PCB, it might free up enough space to fit the ESP32 as a breakaway module.

#### 24/02/2022

18. Changed power MOSFETs for dc/dc on/off control for logic level SOT-23 devices to save PCB space.
19. Successfuly reconfigured board with AtMega MCU on main board, and ESP for wifi functions on removeable module. [^daughterboard]

#### 02/03/2022

20. Changed 5V power to ACS712 from 5V_BUS to MCU_5v.
21. Increased size of 12v bus to 6.5mm for <20degC heating at 20A
22. Increased size of 5v bus to 4.8mm for <20degC heating at 16A
23. Changed GND pad connections to GND plane to solid
24. Changed hirachical sheets to include GNDPWR and GND. This make it easier to route different connections using different netclasses to account for different current requirements 
for each trace. This system seems very imperfect, but I cannot find another workaround.
25 changed clearance for 12V_BUS and GNDPWR from 0.2mm to 0.1985 - Difference seems negligable but passes DRC.

KiCAD feature suggestion - Net Class Labels. I would like to be able to specifiy that 2 nets are joined at any point, but apply different rules on different parts of the net.
Current workaround - Manually change the thickness of the traces after routing. Downside: time, care needed., DRC checks? 

### 28/04/2022 DESIGN REVIEW TODO:

Look up thermal management high current pin connections to GND plane

increase track width 7mm for 20degC temp rise with 0.035  @ 20A

24V bus rate for 35A

5v bus make sure rated for 15A  @20degC rise

practicable io logo

signature

get quote from JLC & PCB way

##### TODO:

## Change Notes

[^1]: Add independent overvoltage protection to 5V_BUS? 		[Zener Diode Overvoltage Protection - Sparkfun](https://www.rs-online.com/designspark/how-does-zener-diode-do-overvoltage-protection-in-circuit#:~:text=In%20order%20to%20protect%20the,flow%20in%20the%20reverse%20direction).
PROBLEM: Suggested 100r resistor between 5v and raspberry pi, this limits current to 50mA, raspi requires min 400mA (Tested with raspi 512mb, raspi4 will likely require more current) 
if R=12.5 is selected, Imax would be 400mA, however power disspation in the resistor is now 0.4\*5 = 2W.

[^daughterboard]: Board is too overloaded to fit everything, there are several courses of action:
1. Remove features.
2. Pick Smaller components
3. implment the same features using less components.
4. daughterboards, requiring carefully cutting nets between sections of the PCB such that it can be re-implemented using pin headers.
	- Note, the use of hirachical sheets should make this process far easier, with the caviat that the use of Global labels may have made this more difficult.
	TODO:
	- Step 1: replace all global power labels in hirarchical sheets with LOCAL net labels. I dont like the use of net labels for joining wires as I beleive it is less clear when
	reading the schematic, however this avoids the issue of having global labels connect "In the background"
	- Step 2: Break nets going between main and MCU hirachical sheet, and rejoin them using pin headers.

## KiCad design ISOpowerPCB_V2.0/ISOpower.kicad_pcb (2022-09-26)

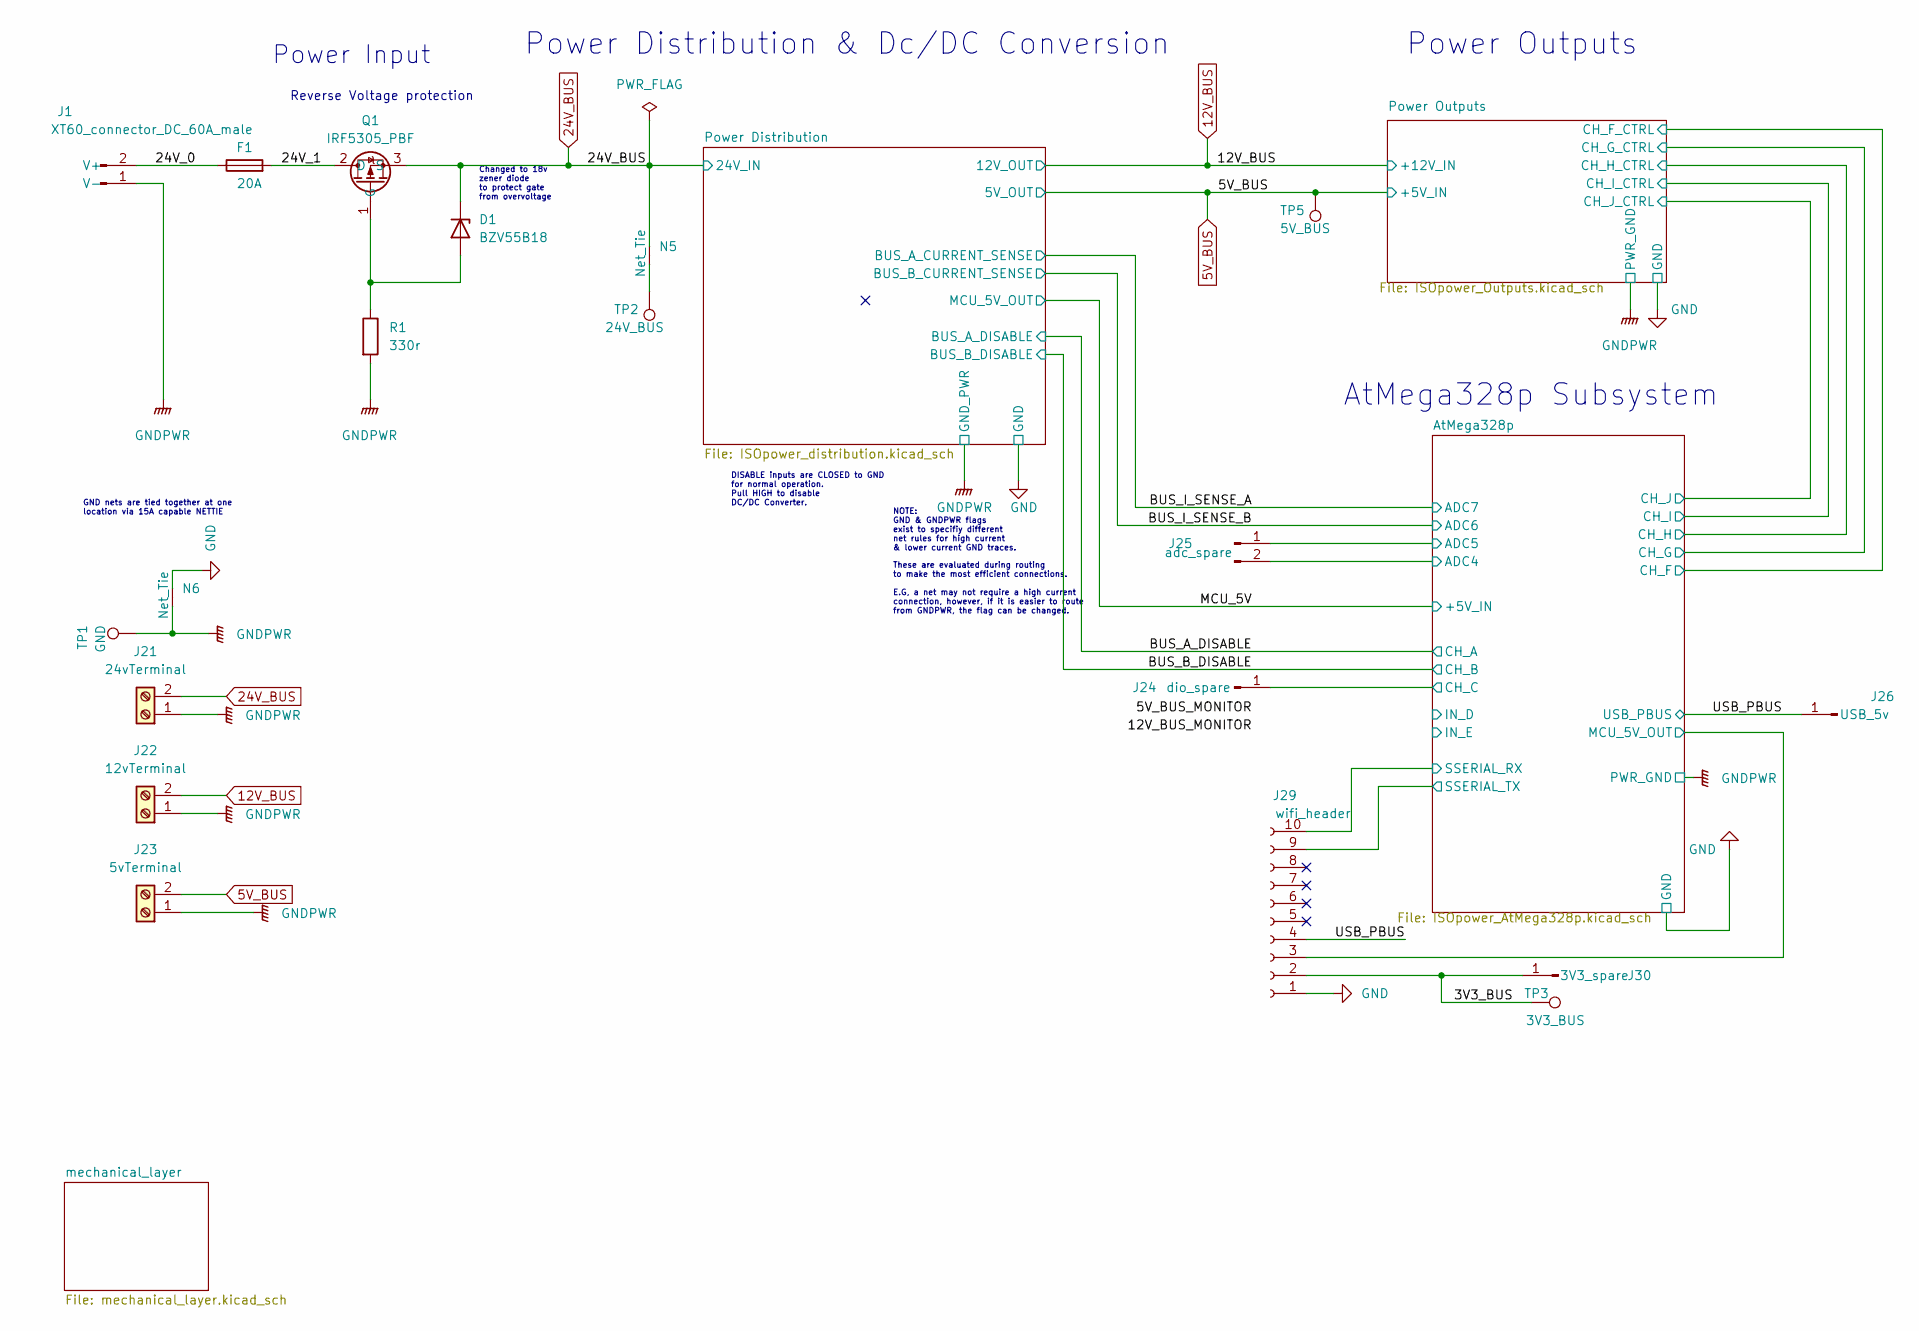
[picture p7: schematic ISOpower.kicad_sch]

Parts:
D1: BZV55B18; D_MiniMELF_Handsoldering
F1: 20A; Fuseholder_Cylinder-5x20mm_Stelvio-Kontek_PTF78_Horizontal_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
J1: XT60_connector_DC_60A_male; AMASS_XT60PW-M
J21: 24vTerminal; TerminalBlock_Altech_AK300-2_P5.00mm
J22: 12vTerminal; TerminalBlock_Altech_AK300-2_P5.00mm
J23: 5vTerminal; TerminalBlock_Altech_AK300-2_P5.00mm
J24: dio_spare; PinHeader_1x01_P1.27mm_Vertical
J25: adc_spare; PinHeader_1x02_P1.27mm_Vertical
J26: USB_5v; PinHeader_1x01_P1.27mm_Vertical
J29: wifi_header; PinSocket_1x10_P1.27mm_Vertical
J30: 3V3_spare; PinHeader_1x01_P1.27mm_Vertical
N5: Net_Tie; NetTie-2_SMD_Pad0.5mm
N6: Net_Tie; NetTie-8-15A_1oz_2oz
Q1: IRF5305_PBF; TO-263-2
R1: 330r; R_0805_2012Metric_Pad1.20x1.40mm_HandSolder
TP1: GND; TestPoint_Pad_D1.5mm
TP2: 24V_BUS; TestPoint_Pad_D1.5mm
TP3: 3V3_BUS; TestPoint_Pad_D1.5mm
TP5: 5V_BUS; TestPoint_Pad_D1.5mm

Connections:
5V_BUS: J23.2, TP5.1; also elsewhere on the board
12V_BUS: J22.2; also elsewhere on the board
24V_BUS: D1.1 (K), J21.2, N5.2 (C), Q1.3 (S); also elsewhere on the board
/3V3_BUS: J29.2, J30.1, TP3.1
/24V_0: F1.1, J1.2 (V+)
/24V_1: F1.2, Q1.2 (D)
/AtMega328p/ADC4: J25.2; also elsewhere on the board
/AtMega328p/ADC5: J25.1; also elsewhere on the board
/AtMega328p/CH_C: J24.1; also elsewhere on the board
/AtMega328p/MCU_5V_BUS: J29.3; also elsewhere on the board
/AtMega328p/SSERIAL_RX: J29.10; also elsewhere on the board
/AtMega328p/SSERIAL_TX: J29.9; also elsewhere on the board
/USB_PBUS: J26.1, J29.4; also elsewhere on the board
GND: J29.1, N6.2 (C); also elsewhere on the board
GNDPWR: J1.1 (V-), J21.1, J22.1, J23.1, N6.1 (A), R1.2, TP1.1; also elsewhere on the board
unnamed: D1.2 (A), Q1.1 (G), R1.1
unnamed: N5.1 (A), TP2.1

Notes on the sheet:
Power Outputs
Reverse Voltage protection
AtMega328p Subsystem
Power Distribution & Dc/DC Conversion
Power Input
DISABLE inputs are CLOSED to GND for normal operation. Pull HIGH to disable DC/DC Converter.
NOTE: GND & GNDPWR flags exist to specifiy different net rules for high current & lower current GND traces.
Changed to 18v zener diode to protect gate from overvoltage
These are evaluated during routing to make the most efficient connections. E.G, a net may not require a high current connection, however, if it is easier to route from GNDPWR, the flag can be changed.
GND nets are tied together at one location via 15A capable NETTIE

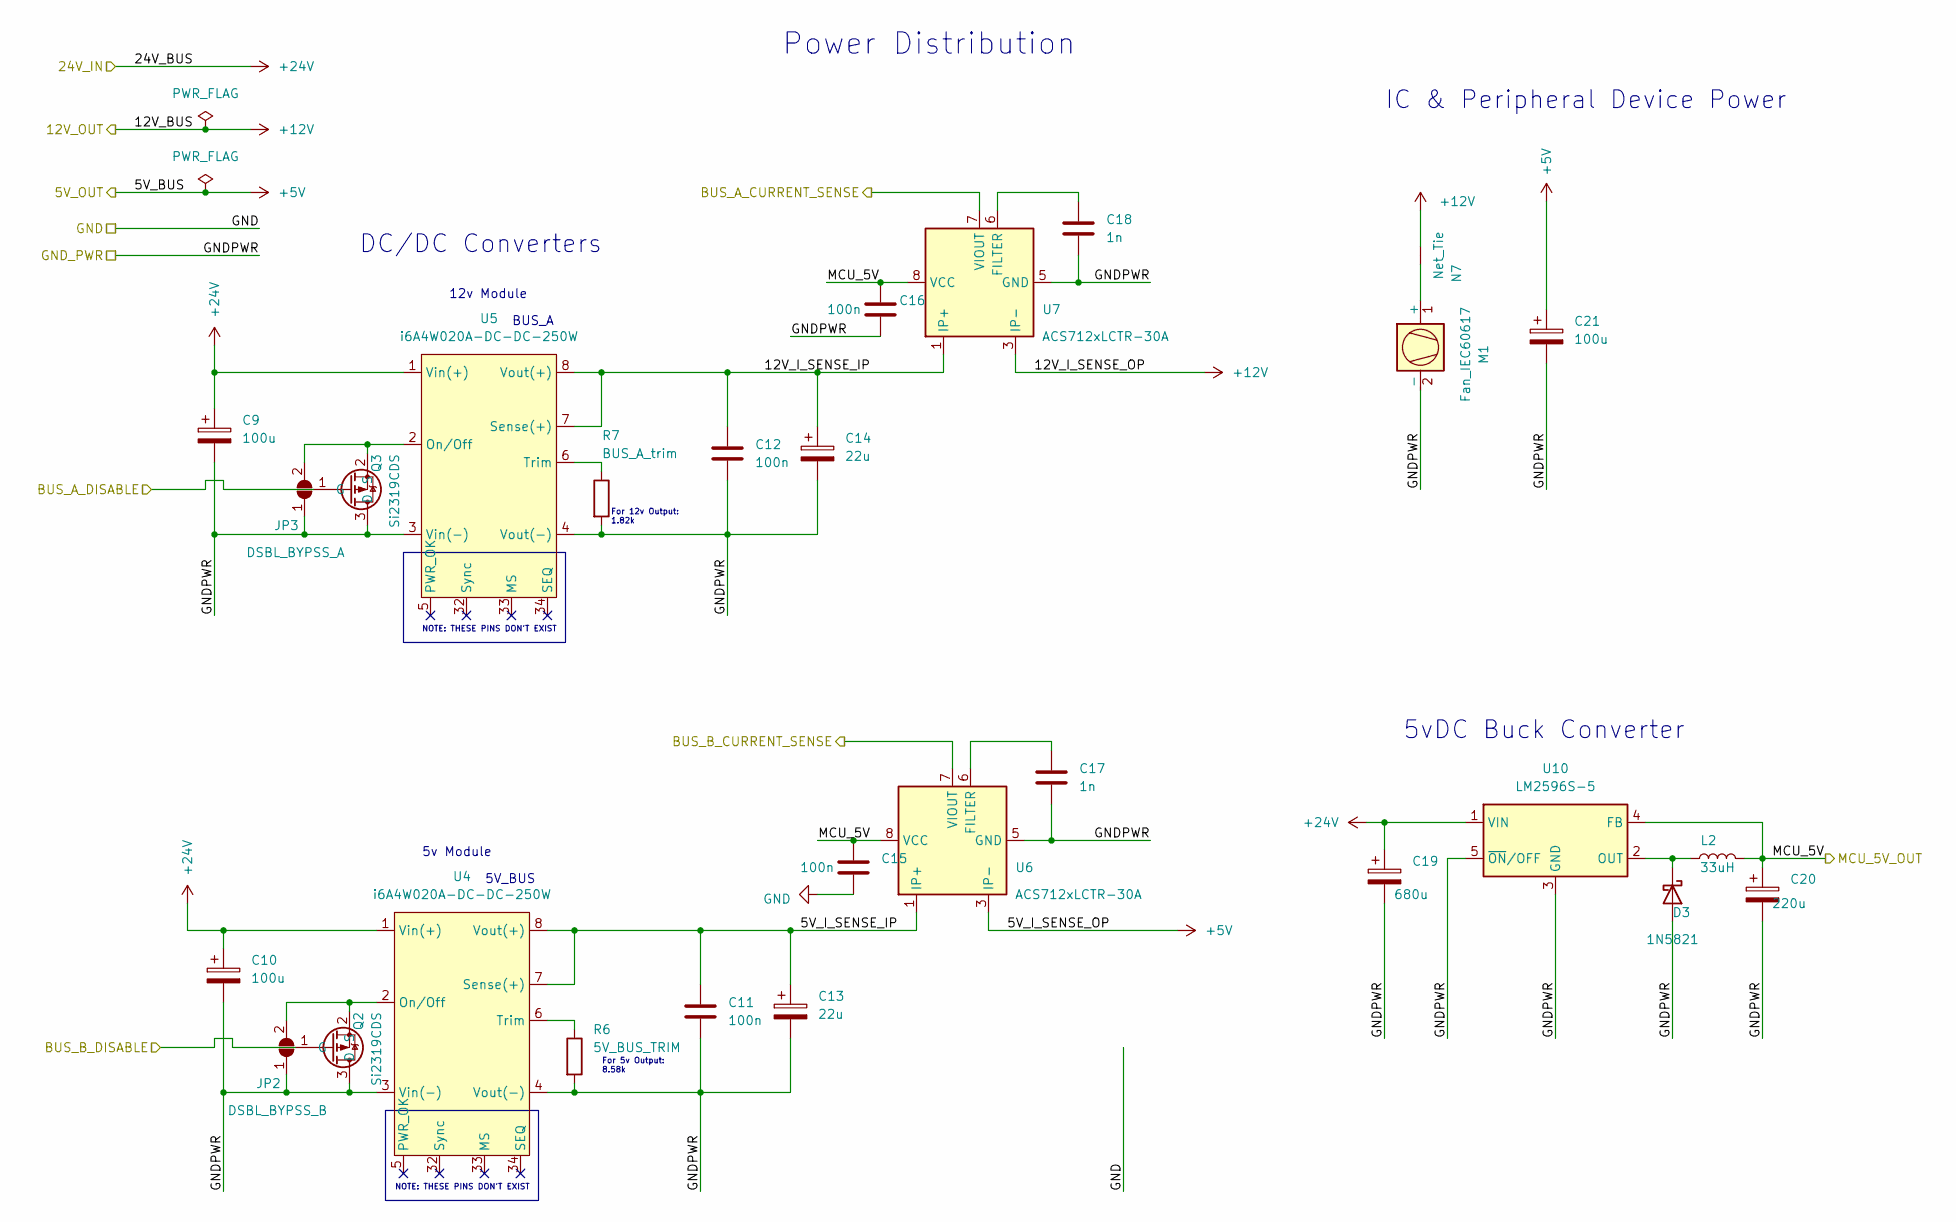
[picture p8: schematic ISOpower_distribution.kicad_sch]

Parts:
C9, C10, C21: 100u; CP_Elec_6.3x7.7
C11, C12, C15, C16: 100n; C_0805_2012Metric_Pad1.18x1.45mm_HandSolder
C13, C14: 22u; CP_Elec_6.3x5.4
C17, C18: 1n; C_0805_2012Metric_Pad1.18x1.45mm_HandSolder
C19: 680u; C_Radial_D12.5mm_H20.0mm_P5.00mm
C20: 220u; CP_Elec_6.3x7.7
D3: 1N5821; D_SMA
JP2: DSBL_BYPSS_B; SolderJumper-2_P1.3mm_Open_RoundedPad1.0x1.5mm
JP3: DSBL_BYPSS_A; SolderJumper-2_P1.3mm_Open_RoundedPad1.0x1.5mm
L2: 33uH; L_12x12mm_H8mm
M1: Fan_IEC60617; Fan12V_40by10.5mm
N7: Net_Tie; NetTie-2_SMD_Pad0.5mm
Q2, Q3: Si2319CDS; SOT-23
R6: 5V_BUS_TRIM; R_Axial_DIN0207_L6.3mm_D2.5mm_P7.62mm_Horizontal
R7: BUS_A_trim; R_Axial_DIN0207_L6.3mm_D2.5mm_P7.62mm_Horizontal
U4, U5: i6A4W020A-DC-DC-250W; i6A4W-DIP
U6, U7: ACS712xLCTR-30A; SOIC-8_3.9x4.9mm_P1.27mm
U10: LM2596S-5; TO-263-5_TabPin3

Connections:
5V_BUS: C21.1, U6.3 (IP-), U6.4 (IP-); also elsewhere on the board
12V_BUS: N7.2 (C), U7.3 (IP-), U7.4 (IP-); also elsewhere on the board
24V_BUS: C9.1, C10.1, C19.1, U4.1 (Vin(+)), U5.1 (Vin(+)), U10.1 (VIN); also elsewhere on the board
/BUS_A_DISABLE: Q3.1 (G); also elsewhere on the board
/BUS_B_DISABLE: Q2.1 (G); also elsewhere on the board
/BUS_I_SENSE_A: U7.7 (VIOUT); also elsewhere on the board
/BUS_I_SENSE_B: U6.7 (VIOUT); also elsewhere on the board
/MCU_5V: C15.1, C16.1, C20.1, L2.2, U6.8 (VCC), U7.8 (VCC), U10.4 (FB); also elsewhere on the board
/Power Distribution/5V_I_SENSE_IP: C11.1, C13.1, U4.7 (Sense(+)), U4.8 (Vout(+)), U6.1 (IP+), U6.2 (IP+)
/Power Distribution/12V_I_SENSE_IP: C12.1, C14.1, U5.7 (Sense(+)), U5.8 (Vout(+)), U7.1 (IP+), U7.2 (IP+)
GND: C15.2; also elsewhere on the board
GNDPWR: C9.2, C10.2, C11.2, C12.2, C13.2, C14.2, C16.2, C17.2, C18.2, C19.2, C20.2, C21.2, D3.2 (A), JP2.1 (A), JP3.1 (A), M1.2 (-), Q2.3 (D), Q3.3 (D), R6.2, R7.2, U4.3 (Vin(-)), U4.4 (Vout(-)), U5.3 (Vin(-)), U5.4 (Vout(-)), U6.5 (GND), U7.5 (GND), U10.3 (GND), U10.5 (~ON/OFF); also elsewhere on the board
unnamed: C17.1, U6.6 (FILTER)
unnamed: C18.1, U7.6 (FILTER)
unnamed: D3.1 (K), L2.1, U10.2 (OUT)
unnamed: JP2.2 (B), Q2.2 (S), U4.2 (On/Off)
unnamed: JP3.2 (B), Q3.2 (S), U5.2 (On/Off)
unnamed: M1.1 (+), N7.1 (A)
unnamed: R6.1, U4.6 (Trim)
unnamed: R7.1, U5.6 (Trim)

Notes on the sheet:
For 5v Output: 8.58k
12v Module
IC & Peripheral Device Power
NOTE: THESE PINS DON'T EXIST
5v Module
Power Distribution
DC/DC Converters
For 12v Output: 1.82k
5vDC Buck Converter
5V_BUS
BUS_A

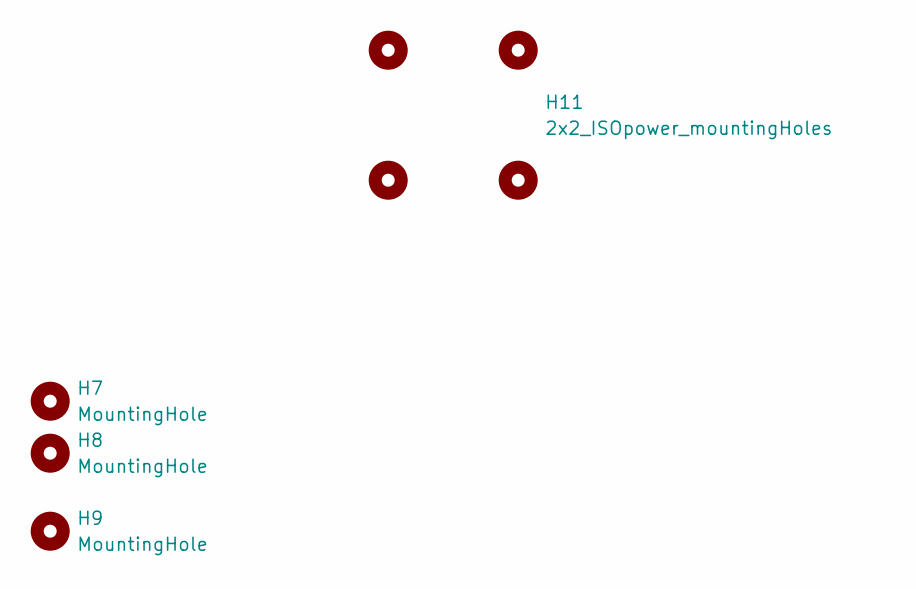
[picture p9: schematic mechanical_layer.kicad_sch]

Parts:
H7, H8, H9: MountingHole; MountingHole_3.2mm_M3
H11: 2x2_ISOpower_mountingHoles; ISOpower_4xmounting_M3

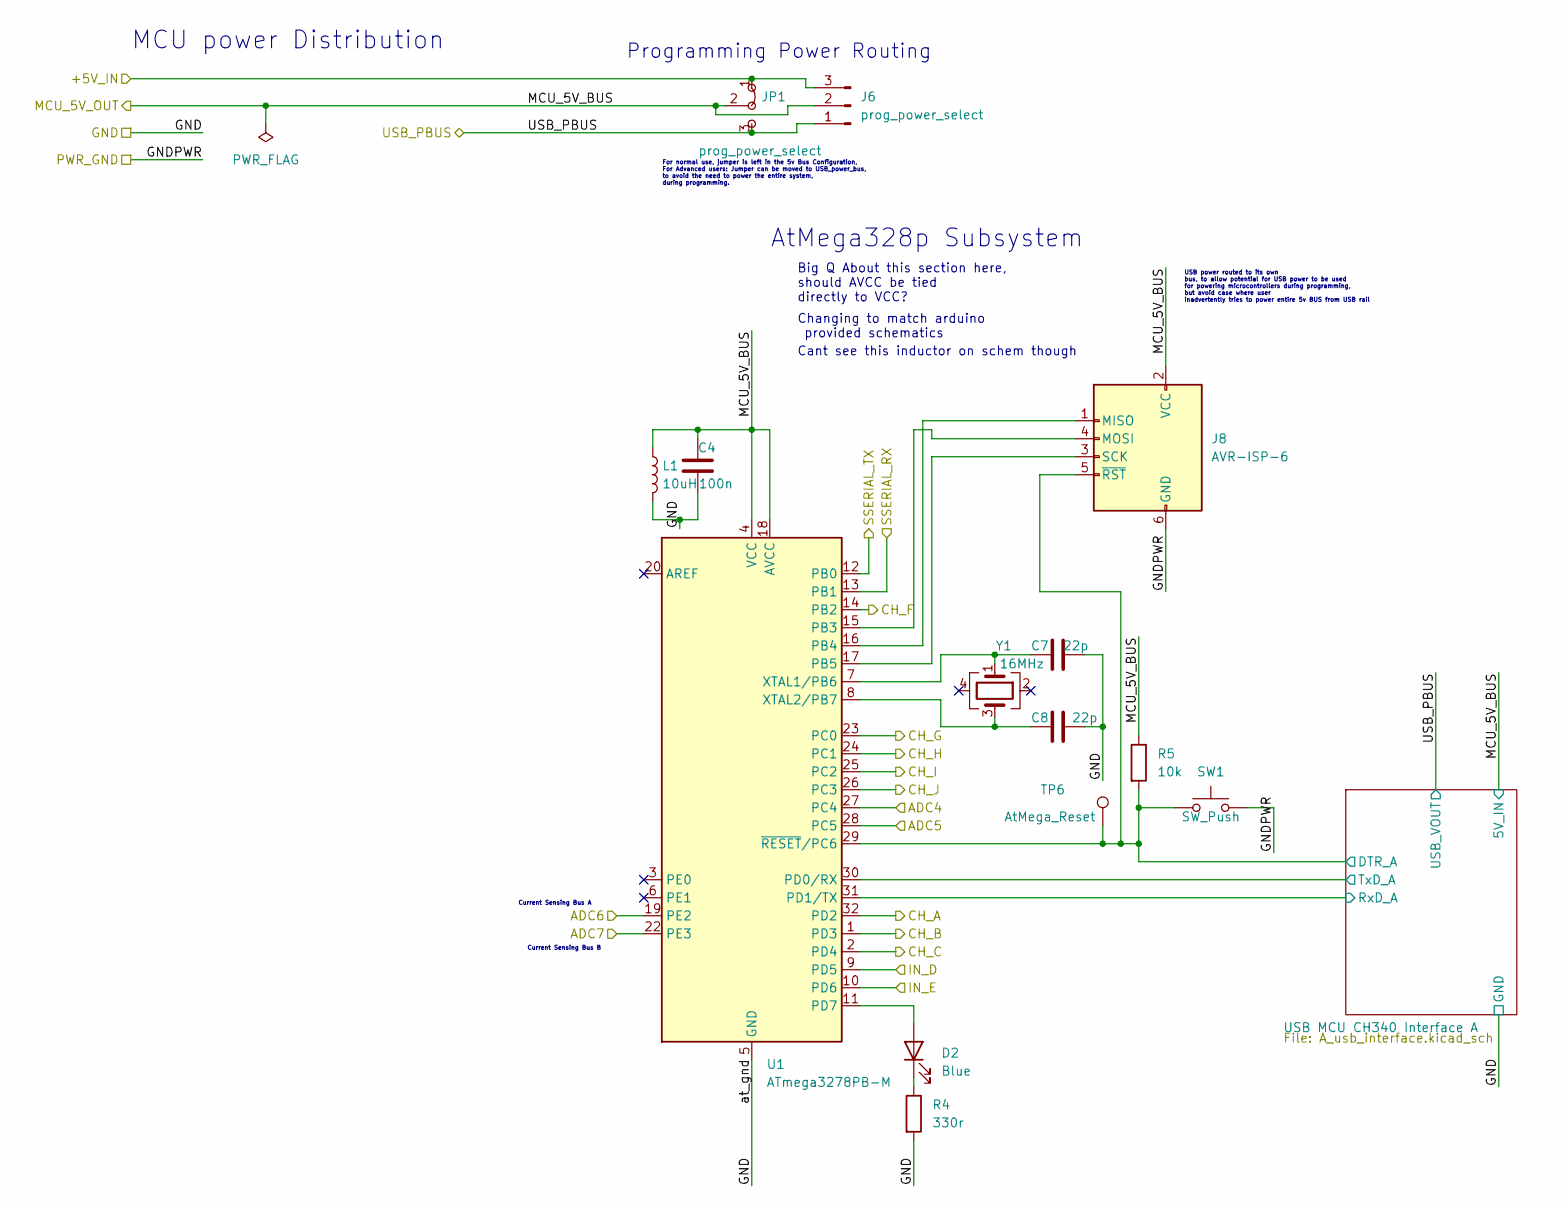
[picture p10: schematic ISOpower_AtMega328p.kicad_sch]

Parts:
C4: 100n; C_0805_2012Metric_Pad1.18x1.45mm_HandSolder
C7, C8: 22p; C_0805_2012Metric_Pad1.18x1.45mm_HandSolder
D2: Blue; LED_0805_2012Metric_Pad1.15x1.40mm_HandSolder
J6: prog_power_select; PinHeader_1x03_P1.27mm_Vertical
J8: AVR-ISP-6; PinHeader_2x03_P1.27mm_Vertical
JP1: prog_power_select; SolderJumper-3_P1.3mm_Bridged12_RoundedPad1.0x1.5mm_NumberL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
L1: 10uH; L_0805_2012Metric_Pad1.05x1.20mm_HandSolder
R4: 330r; R_0805_2012Metric_Pad1.20x1.40mm_HandSolder
R5: 10k; R_0805_2012Metric_Pad1.20x1.40mm_HandSolder
SW1: SW_Push; SW_SPST_EVQPE1
TP6: AtMega_Reset; TestPoint_Pad_D1.5mm
U1: ATmega3278PB-M; QFN-32-1EP_5x5mm_P0.5mm_EP3.1x3.1mm
Y1: 16MHz; Crystal_SMD_Abracon_ABM3C-4Pin_5.0x3.2mm

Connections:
/AtMega328p/ADC4: U1.27 (PC4); also elsewhere on the board
/AtMega328p/ADC5: U1.28 (PC5); also elsewhere on the board
/AtMega328p/CH_C: U1.2 (PD4); also elsewhere on the board
/AtMega328p/CH_F: U1.14 (PB2); also elsewhere on the board
/AtMega328p/CH_G: U1.23 (PC0); also elsewhere on the board
/AtMega328p/CH_H: U1.24 (PC1); also elsewhere on the board
/AtMega328p/CH_I: U1.25 (PC2); also elsewhere on the board
/AtMega328p/CH_J: U1.26 (PC3); also elsewhere on the board
/AtMega328p/IN_D: U1.9 (PD5)
/AtMega328p/IN_E: U1.10 (PD6)
/AtMega328p/MCU_5V_BUS: C4.1, J6.2, J8.2 (VCC), JP1.2 (C), L1.1, R5.1, U1.4 (VCC), U1.18 (AVCC); also elsewhere on the board
/AtMega328p/SSERIAL_RX: U1.13 (PB1); also elsewhere on the board
/AtMega328p/SSERIAL_TX: U1.12 (PB0); also elsewhere on the board
/AtMega328p/USB MCU CH340 Interface A/DTR_A: J8.5 (~RST), R5.2, SW1.1, TP6.1, U1.29 (~RESET/PC6); also elsewhere on the board
/AtMega328p/USB MCU CH340 Interface A/RxD_A: U1.31 (PD1/TX); also elsewhere on the board
/AtMega328p/USB MCU CH340 Interface A/TxD_A: U1.30 (PD0/RX); also elsewhere on the board
/BUS_A_DISABLE: U1.32 (PD2); also elsewhere on the board
/BUS_B_DISABLE: U1.1 (PD3); also elsewhere on the board
/BUS_I_SENSE_A: U1.22 (PE3); also elsewhere on the board
/BUS_I_SENSE_B: U1.19 (PE2); also elsewhere on the board
/MCU_5V: J6.3, JP1.1 (A); also elsewhere on the board
/USB_PBUS: J6.1, JP1.3 (B); also elsewhere on the board
GND: C4.2, C7.2, C8.2, L1.2, R4.2, U1.5 (GND), U1.21 (GND), U1.33 (GND); also elsewhere on the board
GNDPWR: J8.6 (GND), SW1.2; also elsewhere on the board
unnamed: C7.1, U1.7 (XTAL1/PB6), Y1.1
unnamed: C8.1, U1.8 (XTAL2/PB7), Y1.3
unnamed: D2.1 (K), R4.1
unnamed: D2.2 (A), U1.11 (PD7)
unnamed: J8.1 (MISO), U1.16 (PB4)
unnamed: J8.3 (SCK), U1.17 (PB5)
unnamed: J8.4 (MOSI), U1.15 (PB3)

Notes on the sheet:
AtMega328p Subsystem
MCU power Distribution
USB power routed to its own bus, to allow potential for USB power to be used for powering microcontrollers during programming, but avoid case where user inadvertently tries to power entire 5v BUS from USB rail
Big Q About this section here, should AVCC be tied directly to VCC?
Cant see this inductor on schem though
Current Sensing Bus B
Changing to match arduino provided schematics
For normal use, jumper is left in the 5v Bus Configuration, For Advanced users: Jumper can be moved to USB_power_bus, to avoid the need to power the entire system, during programming.
Current Sensing Bus A
Programming Power Routing

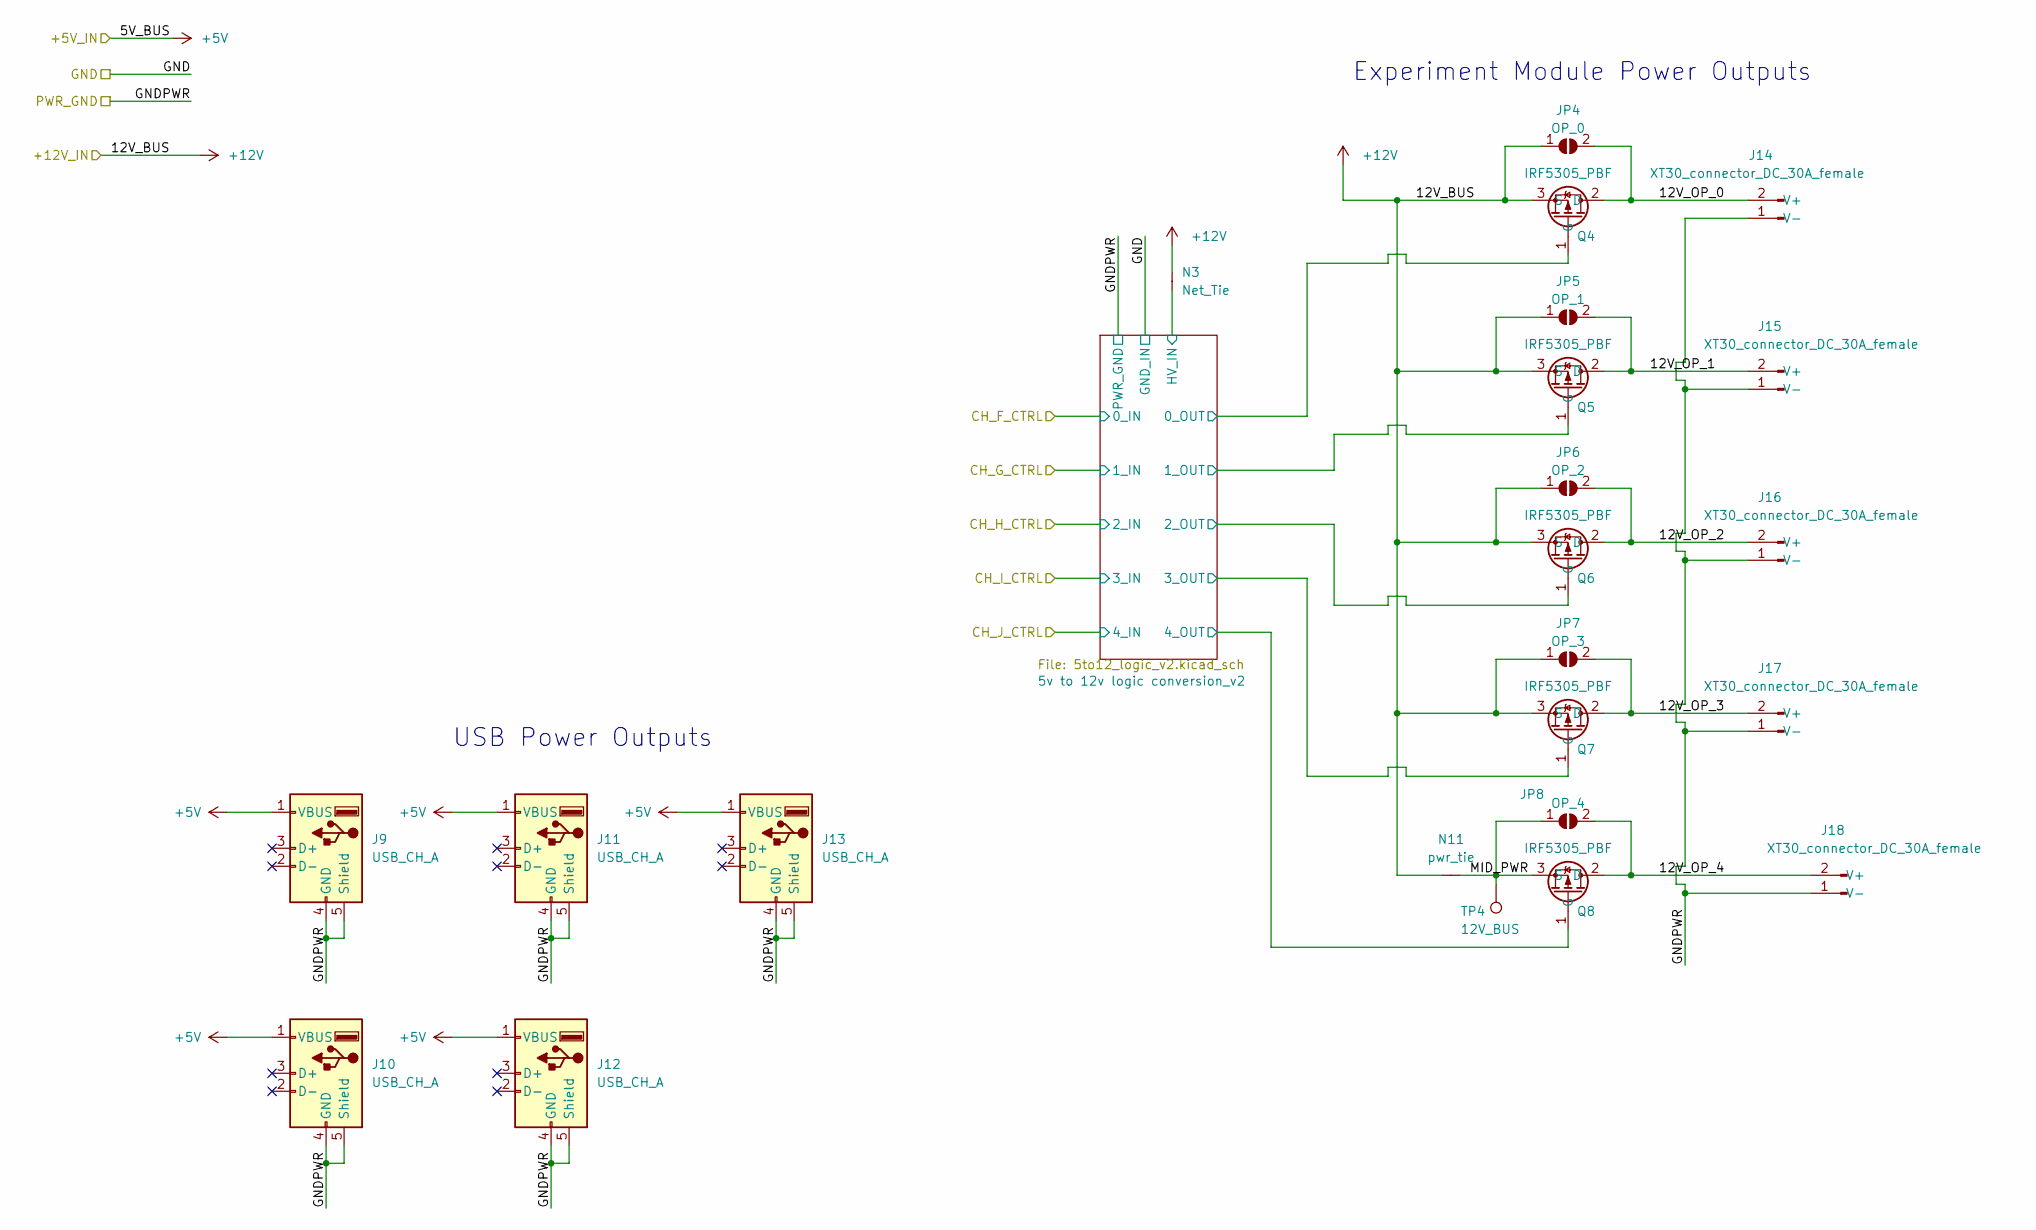
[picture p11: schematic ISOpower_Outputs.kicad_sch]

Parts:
J9, J10, J11, J12, J13: USB_CH_A; USB_A_Molex_67643_Horizontal
J14, J15, J16, J17, J18: XT30_connector_DC_30A_female; AMASS_XT30PW-F_1x02_P2.50mm_Horizontal
JP4: OP_0; SolderJumper-2_P1.3mm_Open_RoundedPad1.0x1.5mm
JP5: OP_1; SolderJumper-2_P1.3mm_Open_RoundedPad1.0x1.5mm
JP6: OP_2; SolderJumper-2_P1.3mm_Open_RoundedPad1.0x1.5mm
JP7: OP_3; SolderJumper-2_P1.3mm_Open_RoundedPad1.0x1.5mm
JP8: OP_4; SolderJumper-2_P1.3mm_Open_RoundedPad1.0x1.5mm
N3: Net_Tie; NetTie-2_SMD_Pad0.5mm
N11: pwr_tie; NetTie-8-15A_1oz_2oz_chamf
Q4, Q5, Q6, Q7, Q8: IRF5305_PBF; TO-263-2
TP4: 12V_BUS; TestPoint_Pad_D1.5mm

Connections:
5V_BUS: J9.1 (VBUS), J10.1 (VBUS), J11.1 (VBUS), J12.1 (VBUS), J13.1 (VBUS); also elsewhere on the board
12V_BUS: JP4.1 (A), JP5.1 (A), JP6.1 (A), JP7.1 (A), N3.2 (C), N11.1 (A), Q4.3 (S), Q5.3 (S), Q6.3 (S), Q7.3 (S); also elsewhere on the board
/Power Outputs/5v to 12v logic conversion_v2/0_OUT: Q4.1 (G); also elsewhere on the board
/Power Outputs/5v to 12v logic conversion_v2/1_OUT: Q5.1 (G); also elsewhere on the board
/Power Outputs/5v to 12v logic conversion_v2/2_OUT: Q6.1 (G); also elsewhere on the board
/Power Outputs/5v to 12v logic conversion_v2/3_OUT: Q7.1 (G); also elsewhere on the board
/Power Outputs/5v to 12v logic conversion_v2/4_OUT: Q8.1 (G); also elsewhere on the board
/Power Outputs/12V_OP_0: J14.2 (V+), JP4.2 (B), Q4.2 (D)
/Power Outputs/12V_OP_1: J15.2 (V+), JP5.2 (B), Q5.2 (D)
/Power Outputs/12V_OP_2: J16.2 (V+), JP6.2 (B), Q6.2 (D)
/Power Outputs/12V_OP_3: J17.2 (V+), JP7.2 (B), Q7.2 (D)
/Power Outputs/12V_OP_4: J18.2 (V+), JP8.2 (B), Q8.2 (D)
/Power Outputs/MID_PWR: JP8.1 (A), N11.2 (C), Q8.3 (S), TP4.1
GNDPWR: J9.4 (GND), J9.5 (Shield), J10.4 (GND), J10.5 (Shield), J11.4 (GND), J11.5 (Shield), J12.4 (GND), J12.5 (Shield), J13.4 (GND), J13.5 (Shield), J14.1 (V-), J15.1 (V-), J16.1 (V-), J17.1 (V-), J18.1 (V-); also elsewhere on the board
HV: N3.1 (A); also elsewhere on the board

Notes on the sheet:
USB Power Outputs
Experiment Module Power Outputs

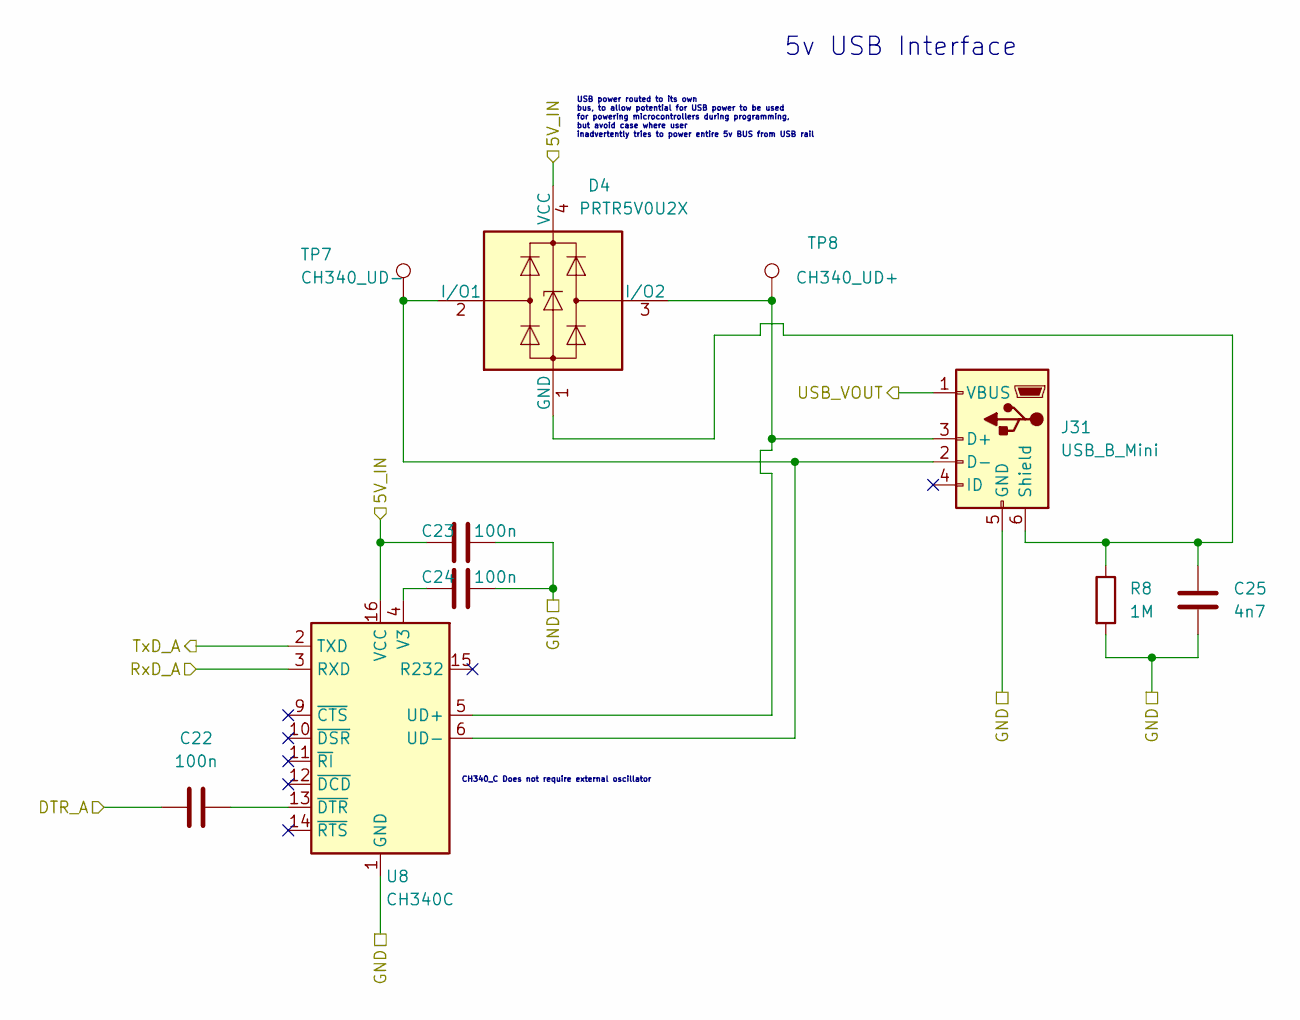
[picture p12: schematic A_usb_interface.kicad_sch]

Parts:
C22, C23, C24: 100n; C_0805_2012Metric_Pad1.18x1.45mm_HandSolder
C25: 4n7; C_0805_2012Metric_Pad1.18x1.45mm_HandSolder
D4: PRTR5V0U2X; SOT-143
J31: USB_B_Mini; USB_Mini-B_Lumberg_2486_01_Horizontal
R8: 1M; R_0805_2012Metric_Pad1.20x1.40mm_HandSolder
TP7: CH340_UD-; TestPoint_Pad_D1.5mm
TP8: CH340_UD+; TestPoint_Pad_D1.5mm
U8: CH340C; SOIC-16_3.9x9.9mm_P1.27mm

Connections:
/AtMega328p/MCU_5V_BUS: C23.1, D4.4 (VCC), U8.16 (VCC); also elsewhere on the board
/AtMega328p/USB MCU CH340 Interface A/DTR_A: C22.1; also elsewhere on the board
/AtMega328p/USB MCU CH340 Interface A/RxD_A: U8.3 (RXD); also elsewhere on the board
/AtMega328p/USB MCU CH340 Interface A/TxD_A: U8.2 (TXD); also elsewhere on the board
/USB_PBUS: J31.1 (VBUS); also elsewhere on the board
GND: C23.2, C24.2, C25.1, J31.5 (GND), R8.2, U8.1 (GND); also elsewhere on the board
unnamed: C22.2, U8.13 (~DTR)
unnamed: C24.1, U8.4 (V3)
unnamed: C25.2, D4.1 (GND), J31.6 (Shield), R8.1
unnamed: D4.2 (I/O1), J31.2 (D-), TP7.1, U8.6 (UD-)
unnamed: D4.3 (I/O2), J31.3 (D+), TP8.1, U8.5 (UD+)

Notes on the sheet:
CH340_C Does not require external oscillator
USB power routed to its own bus, to allow potential for USB power to be used for powering microcontrollers during programming, but avoid case where user inadvertently tries to power entire 5v BUS from USB rail
5v USB Interface

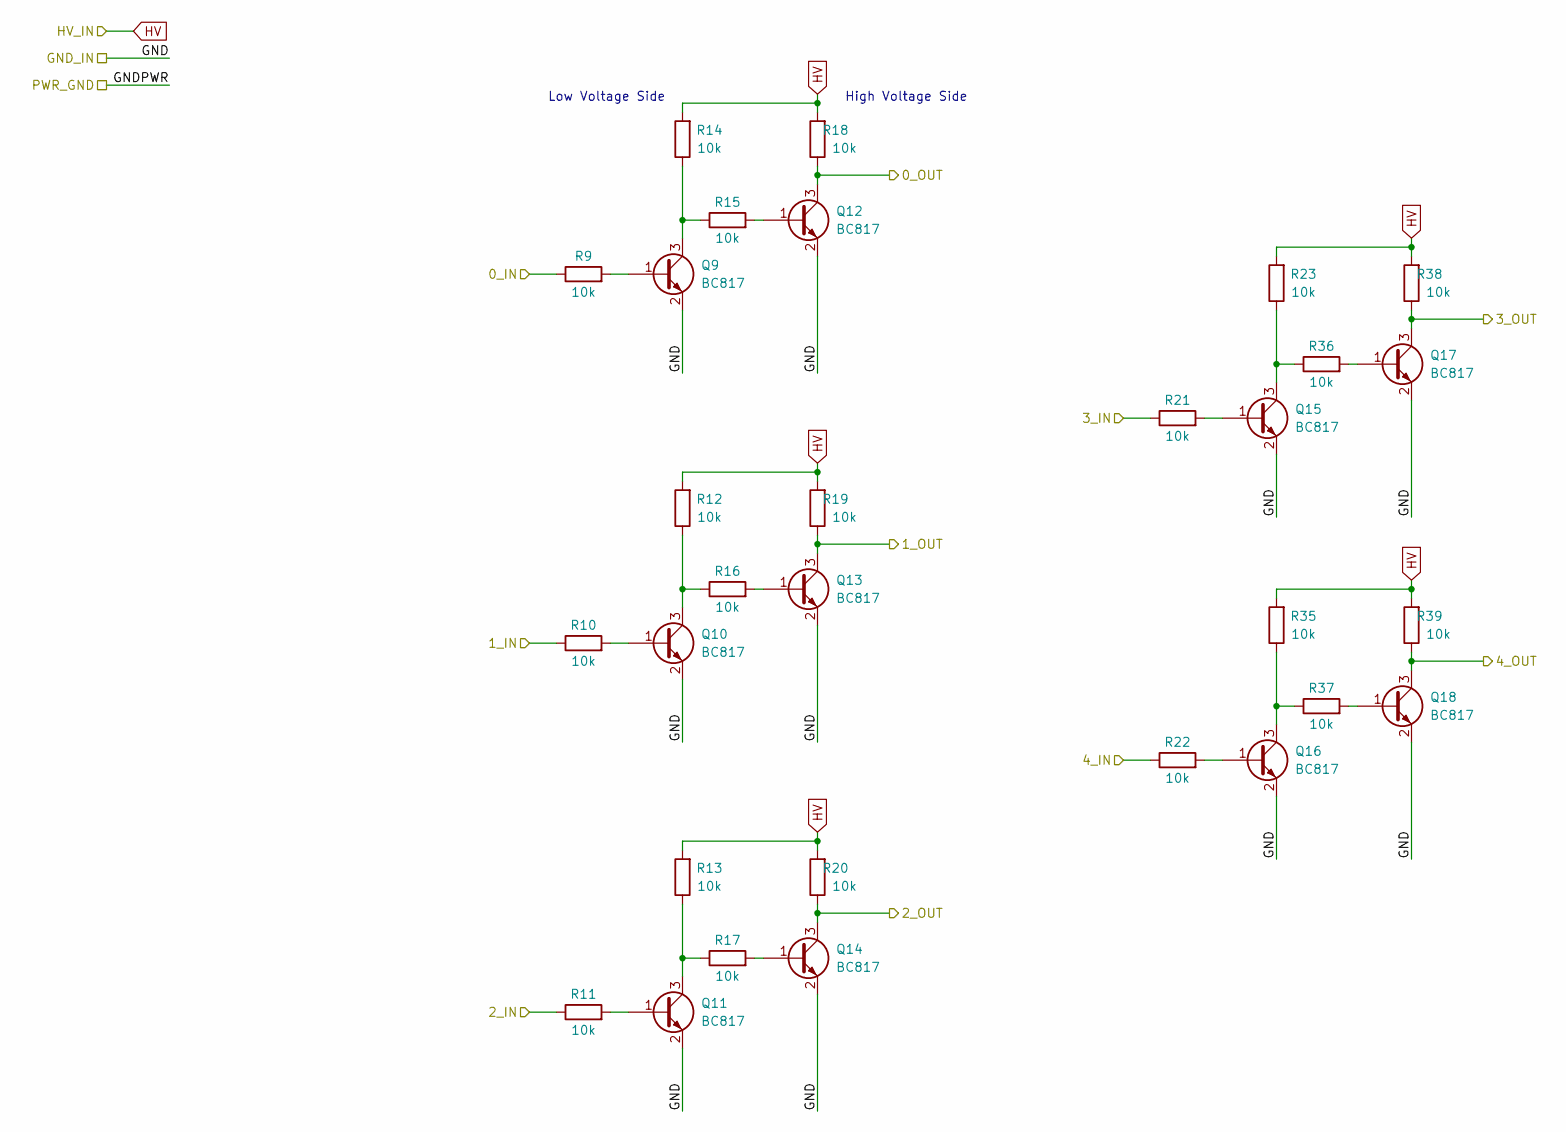
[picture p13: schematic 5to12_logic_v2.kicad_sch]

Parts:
Q9, Q10, Q11, Q12, Q13, Q14, Q15, Q16, Q17, Q18: BC817; SOT-23
R9, R10, R11, R12, R13, R14, R15, R16, R17, R18, R19, R20, R21, R22, R23, R35, R36, R37, R38, R39: 10k; R_0805_2012Metric_Pad1.20x1.40mm_HandSolder

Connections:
/AtMega328p/CH_F: R9.1; also elsewhere on the board
/AtMega328p/CH_G: R10.1; also elsewhere on the board
/AtMega328p/CH_H: R11.1; also elsewhere on the board
/AtMega328p/CH_I: R21.1; also elsewhere on the board
/AtMega328p/CH_J: R22.1; also elsewhere on the board
/Power Outputs/5v to 12v logic conversion_v2/0_OUT: Q12.3 (C), R18.1; also elsewhere on the board
/Power Outputs/5v to 12v logic conversion_v2/1_OUT: Q13.3 (C), R19.1; also elsewhere on the board
/Power Outputs/5v to 12v logic conversion_v2/2_OUT: Q14.3 (C), R20.1; also elsewhere on the board
/Power Outputs/5v to 12v logic conversion_v2/3_OUT: Q17.3 (C), R38.1; also elsewhere on the board
/Power Outputs/5v to 12v logic conversion_v2/4_OUT: Q18.3 (C), R39.1; also elsewhere on the board
GND: Q9.2 (E), Q10.2 (E), Q11.2 (E), Q12.2 (E), Q13.2 (E), Q14.2 (E), Q15.2 (E), Q16.2 (E), Q17.2 (E), Q18.2 (E); also elsewhere on the board
HV: R12.2, R13.2, R14.2, R18.2, R19.2, R20.2, R23.2, R35.2, R38.2, R39.2; also elsewhere on the board
unnamed: Q9.1 (B), R9.2
unnamed: Q9.3 (C), R14.1, R15.1
unnamed: Q10.1 (B), R10.2
unnamed: Q10.3 (C), R12.1, R16.1
unnamed: Q11.1 (B), R11.2
unnamed: Q11.3 (C), R13.1, R17.1
unnamed: Q12.1 (B), R15.2
unnamed: Q13.1 (B), R16.2
unnamed: Q14.1 (B), R17.2
unnamed: Q15.1 (B), R21.2
unnamed: Q15.3 (C), R23.1, R36.1
unnamed: Q16.1 (B), R22.2
unnamed: Q16.3 (C), R35.1, R37.1
unnamed: Q17.1 (B), R36.2
unnamed: Q18.1 (B), R37.2

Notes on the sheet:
Low Voltage Side
High Voltage Side

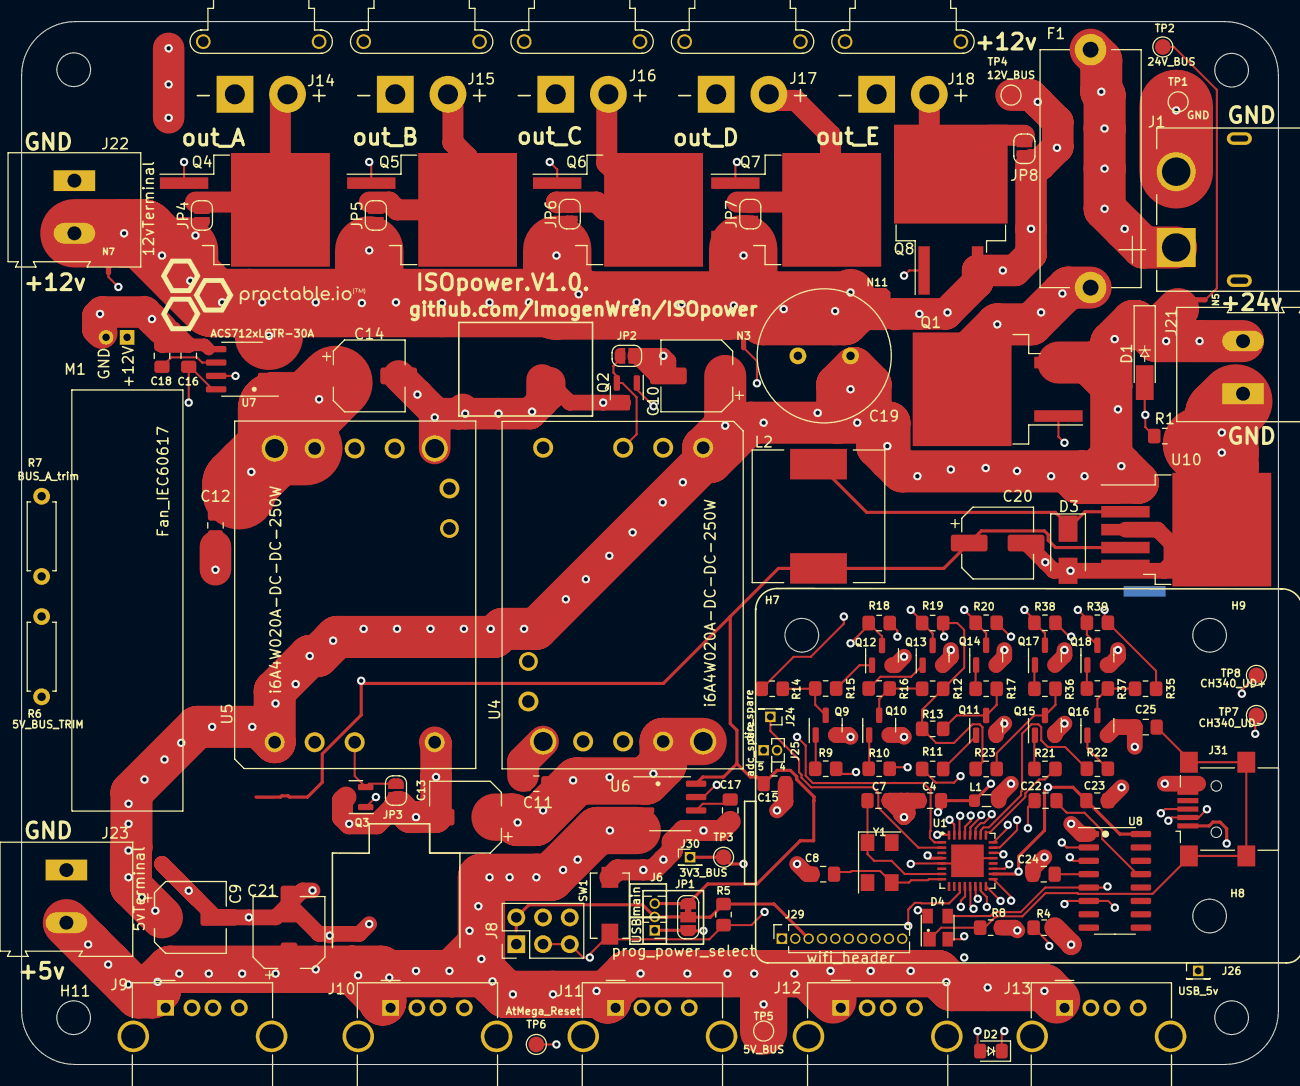
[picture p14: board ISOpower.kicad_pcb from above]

Board: 4 copper layers, 119.4 x 99.1 mm, 128 parts (1 on the bottom side), 79 nets.

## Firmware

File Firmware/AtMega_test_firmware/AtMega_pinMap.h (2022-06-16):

/*  AtMega_pinMap.h

     Translates schematic pin numbers into Arduino digital pin numbers
     and register numbers for pins not available on arduino nano board




*/

#ifndef AtMega_pinMap_h
#define AtMega_pinMap_h



  
#define BUS_12V_DISABLE        2       // HIGH to Disable - I Think
#define BUS_5V_DISABLE         3       // HIGH to Disable
#define CH_C                   4

#define BUS_5V_MONITOR         5       //BUS_5V_MONITOR
#define BUS_12V_MONITOR        6       // BUS_12V_MONITOR

#define LED_PIN               7  


 //Depreciated but not harming anybody
#define CH_A                  2        //BUS_12V_DISABLE              // HIGH to Disable
#define CH_B                  3        //BUS_5V_DISABLE               // HIGH to Disable
#define CH_C                  4

#define IN_D                  5        //BUS_5V_MONITOR
#define IN_E                  6        //BUS_12V_MONITOR

        

// Experiment Output Channels         // HIGH to Disable- (I Think)
#define CH_F                  10
#define CH_G                  A0
#define CH_H                  A1
#define CH_I                  A2
#define CH_J                  A3

int outputChannels[5] = {CH_F, CH_G, CH_H, CH_I, CH_J} ;

#define ADC4                  A4             //Spare
#define ADC5                  A5             //Spare

#define CURRENT_SENSE_12V     A6
#define CURRENT_SENSE_5V      A7






#endif

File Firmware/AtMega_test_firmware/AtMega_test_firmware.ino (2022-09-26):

/*  ISO Power AtMega Test Firmware


    Basic program to test IO Functions and verify PCB is correct

    Imogen Wren
    08/06/2022

   Compile software for Arduino Nano 16MHz


   To Program Remove Wifi Header and use   

   
*/


#include <autoDelay.h>


#include "AtMega_pinMap.h"

#include "currentSense.h"









void ISOpowerBegin(int32_t baudrate = 115200) {
  Serial.begin(baudrate);
  Serial.print("ISO Power Test Firmware");

  //Outputs
  pinMode(BUS_12V_DISABLE, OUTPUT);
  pinMode(BUS_5V_DISABLE, OUTPUT);
  pinMode(LED_PIN, OUTPUT);

  for (int i = 0; i < 5; i++) {
    pinMode(outputChannels[i], OUTPUT);
  }
  //Inputs
  //  pinMode(BUS_5V_MONITOR, INPUT);    //Analog I/P do not need setting up as input
  //  pinMode(BUS_12V_MONITOR, INPUT);
}



void changeChannelState(int16_t channelNumber, bool state) {
  digitalWrite(outputChannels[channelNumber], !state);
}

void enable12vBus(bool enable) {
  if (enable) {
    digitalWrite(BUS_12V_DISABLE, LOW);
  } else {
    digitalWrite(BUS_12V_DISABLE, HIGH);
  }
}


void enable5vBus(bool enable) {
  if (enable) {
    digitalWrite(BUS_5V_DISABLE, LOW);
  } else {
    digitalWrite(BUS_5V_DISABLE, HIGH);
  }
}


void flashLED() {
  int loops = 6;
  while (loops > 0) {
    digitalWrite(LED_PIN, HIGH);
    delay(100);
    digitalWrite(LED_PIN, LOW);
    delay(200);
    loops--;
  }
}



void sendByte(uint8_t someData) {
  Serial.println(someData);
}


void startListen() {
  char buffer[64];
  int intBuffer;
  if (Serial.available() > 0) {
    intBuffer = Serial.read();
    Serial.println(intBuffer);
  }
}



void setup() {
  ISOpowerBegin(115200);
  changeChannelState(0, HIGH);
  changeChannelState(1, HIGH);
  changeChannelState(2, HIGH);
  changeChannelState(3, HIGH);
  changeChannelState(4, HIGH);
  enable12vBus(false);
  enable5vBus(false);
  flashLED();

}




autoDelay txDelay;
#define TX_PERIOD 1

void loop() {
//  currentSenseLoop();
 //startListen();
  
 // if (rxVal != 0) {
 //   Serial.println(rxVal);
 // }

///  if (txDelay.secondsDelay(TX_PERIOD)) {
 // sendByte(7);
 // }

}

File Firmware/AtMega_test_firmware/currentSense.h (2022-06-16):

/*  currentSense.h

     Read analog input and convert to current as detected by ACS712 IC



*/


int16_t bus_12v_sample;

int16_t bus_5v_sample;

int16_t bus_12v_current;
int16_t bus_5v_current;

//Constant Values for ACS712-30A (Can change for different models of board)
#define SENSITIVITY  66
#define V_OFFSET  2500

bool newSample;


autoDelay sampleDelay;

#define ADC_SAMPLE_DELAY 500


void sampleADCs() {
  if (sampleDelay.millisDelay(ADC_SAMPLE_DELAY)) {
    bus_12v_sample = analogRead(CURRENT_SENSE_12V);
    bus_5v_sample = analogRead(CURRENT_SENSE_5V);
    newSample = true;
  }
}


int16_t ADCtoVoltage(int16_t adcValue) {
  int16_t adcVoltage = (adcValue / 1023) * 5000;
  return adcVoltage;
}

int16_t voltageToCurrent(int16_t adcVoltage) {
  int16_t currentValue = ((adcVoltage - V_OFFSET) / SENSITIVITY);
  return currentValue;
}




void currentSenseLoop() {
  sampleADCs();
  if (newSample) {
    char buffer[42];
    bus_12v_current = ADCtoVoltage(bus_12v_sample);
    bus_12v_current = voltageToCurrent(bus_12v_current);
    bus_5v_current = ADCtoVoltage(bus_5v_sample);
    bus_5v_current = voltageToCurrent(bus_5v_current);
    sprintf(buffer, "12v Bus Current: %i,  5v BUs Current: %i", bus_12v_current, bus_5v_current);
    Serial.println(buffer);
  }


}

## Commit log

2022-01-24 Reoganised files
    [ISOpower.kicad_pcb, ISOpower.kicad_sch, ISOpower_MCU.kicad_sch, ISOpower_Outputs.kicad_sch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]
2022-01-25 deleted old backups & added documentation
    [A_usb_interface.kicad_sch, B_usb_interface.kicad_sch, ISOpower.kicad_sch, ISOpower_MCU.kicad_sch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]
2022-01-25 modified pcb files
    [A_usb_interface.kicad_sch, B_usb_interface.kicad_sch, ISOpower.kicad_sch, ISOpower_MCU.kicad_sch]
2022-01-26 Finished initial circuit design
    [5to12_logic.kicad_sch, A_usb_interface.kicad_sch, CP2102_USB_MCU_interface.kicad_sch, ISOpower.kicad_sch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]
2022-01-26 PCB Notes added
    [ISOpower.kicad_sch, ISOpower_MCU.kicad_sch, ISOpower_distribution.kicad_sch, logiclevelconverter.kicad_sch]
2022-01-28 Copied old version into version_0.1 folder
    [5to12_logic.kicad_sch, A_usb_interface.kicad_sch, B_usb_interface.kicad_sch, CP2102_USB_MCU_interface.kicad_sch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]
2022-01-28 Major schematic revisions
    [ISOpower.kicad_sch, ISOpower_MCU.kicad_sch, ISOpower_Outputs.kicad_sch, ISOpower_distribution.kicad_sch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]
2022-01-31 significant changes
    [ISOpower.kicad_sch, ISOpower_MCU.kicad_sch, ISOpower_distribution.kicad_sch, ch340_ESP32.kicad_sch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]
2022-02-04 Updated as per discussions 26/01/22
    # Change Notes
    04/02/2022
    As per discussion 26/01/22
    1. Changed per channel 5v MOSFET switches to MOSFET control of DC/DC module on/off pin - due to failure of MOSFET switching during testing.
    2. Added 5v buck converter for independent MCU_5V power bus.
    - Ensured all 5v MCU hardware is powered from common MCU_5V bus.
    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
    [5to12_logic.kicad_sch, 5to12_logic_v2.kicad_sch, A_usb_interface.kicad_sch, ISOpower.kicad_sch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]
2022-02-14 messing around with libraries
    [5to12_logic_v2.kicad_sch, A_usb_interface.kicad_sch, ISOpower.kicad_sch, ISOpower_MCU.kicad_sch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]
2022-02-14 adding logic for fault indication
    [5to12_logic_v2.kicad_sch, A_usb_interface.kicad_sch, ISOpower.kicad_sch, ISOpower_MCU.kicad_sch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]
2022-02-15 uurgh libraries
    [A_usb_interface.kicad_sch, ISOpower.kicad_sch, ISOpower_MCU.kicad_sch, ch340_ESP32.kicad_sch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]
2022-02-15 fixed most electrical rules check violations
    [5to12_logic_v2.kicad_sch, A_usb_interface.kicad_sch, ISOpower.kicad_sch, ISOpower_MCU.kicad_sch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]
2022-02-16 Footprint Associations 50% complete
    [5to12_logic_v2.kicad_sch, A_usb_interface.kicad_sch, ISOpower.kicad_sch, ISOpower_MCU.kicad_sch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]
2022-02-18 added documentation for component selection
    Completed footprint association & added documentation re Netclasses. Need to update netclasses in schematic settings before moving to PCB layout.
    [A_usb_interface.kicad_sch, ISOpower.kicad_pcb, ISOpower.kicad_sch, ISOpower_MCU.kicad_sch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]
2022-02-21 Removed Optical Engine
    Folder inadvertently placed incorrectly
    [OPTICAL_ENGINE.kicad_pcb, OPTICAL_ENGINE.kicad_sch]
2022-02-21 added netclasses
    [ISOpower.kicad_sch, ISOpower_MCU.kicad_sch, ISOpower_Outputs.kicad_sch, ISOpower_distribution.kicad_sch]
2022-02-21 Started PCB Layout
    [5to12_logic_v2.kicad_sch, A_usb_interface.kicad_sch, ISOpower.kicad_pcb, ISOpower.kicad_sch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]
2022-02-22 PCB Layouts
    [5to12_logic_v2.kicad_sch, A_usb_interface.kicad_sch, ISOpower.kicad_pcb, ISOpower.kicad_sch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]
2022-02-23 Components placed V1.0
    [A_usb_interface.kicad_sch, ISOpower.kicad_pcb, ISOpower.kicad_sch, ISOpower_AtMega328p.kicad_sch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]
2022-02-24 Started Routing V1
    [ISOpower.kicad_pcb, ISOpower.kicad_sch, ISOpower_distribution.kicad_sch, v_monitor.kicad_sch]
2022-02-25 PCB layout completed.
    Screenshots added to media folder
    [ISOpower.kicad_pcb, ISOpower.kicad_sch, ISOpower_AtMega328p.kicad_sch, ISOpower_Outputs.kicad_sch]
2022-02-25 added media
    [ISOpower-B_Cu.gbr, ISOpower-B_Mask.gbr, ISOpower-B_Paste.gbr, ISOpower-B_Silkscreen.gbr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]
2022-02-28 finished PCB design. Started design review docs
    [ISOpower.kicad_pcb, ISOpower.kicad_sch, mechanical_layer.kicad_sch]
2022-03-01 Replacing power bus RE current draw issue
    [ISOpower-B_Cu.gbr, ISOpower-B_Mask.gbr, ISOpower-B_Paste.gbr, ISOpower-B_Silkscreen.gbr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]
2022-03-02 almost finished needs to pass DRC check and fix aesthetics
    [ISOpower_Outputs.kicad_sch, ISOpower_distribution.kicad_sch]
2022-03-03 Finished Silkscreen edits
    [ISOpower.kicad_pcb]
2022-03-03 Passed DRC - Board separation into 2 folders next
    [ISOpower-B_Cu.gbr, ISOpower-B_Mask.gbr, ISOpower-B_Paste.gbr, ISOpower-B_Silkscreen.gbr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]
2022-03-03 Producing files for fabrication
    [5to12_logic.kicad_sch, 5to12_logic_v2.kicad_sch, A_usb_interface.kicad_sch, BOM_ISOpowerWiFi_PCB.csv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]
2022-03-04 colating fabrication documents.
    [5to12_logic.kicad_sch, 5to12_logic_v2.kicad_sch, A_usb_interface.kicad_sch, BOM_ISOpower.csv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]
2022-03-07 Adding fabrication files
    [BOM_ISOpower.csv, BOM_ISOpower_PCBway.xlsx, BOM_ISOpower_with_stats.xlsx, ISOpower-B_Cu.gbr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]
2022-03-16 added fabrication files
    [ISOpowerWiFi_PCB-B_Cu.gbr, ISOpowerWiFi_PCB-B_Mask.gbr, ISOpowerWiFi_PCB-B_Paste.gbr, ISOpowerWiFi_PCB-B_Silkscreen.gbr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]
2022-03-25 updated BOM due to semiconductor shortages
    [BOM_ISO_Power_PCB_RS_order.xlsx, BOM_ISO_Power_PCB_final.xls, BOM_ISO_Power_PCB_final.xlsx, T-Y4W418135A-25sets-BOM_ISOpower_PCBway(2022-03-09).xls]
2022-05-13 added first production photos
    [BOM_ISO_Power_PCB_RS_order.xlsx, BOM_ISOpower.csv, ISOpower.csv]
2022-06-08 changes to ACS712 Current sense
2022-09-26 Started work on V2.0
    [5to12_logic.kicad_sch, 5to12_logic_v2.kicad_sch, A_usb_interface.kicad_sch, B_usb_interface.kicad_sch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]
